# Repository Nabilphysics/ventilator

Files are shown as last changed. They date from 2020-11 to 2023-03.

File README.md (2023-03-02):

# Turbine Based Open-source Medical Ventilator [][License]

*A Turbine Based Medical Ventilator*

---
Publication 1: HardwareX :https://www.hardware-x.com/article/S2468-0672(22)00095-5/fulltext </br>
Publication: https://dl.acm.org/doi/abs/10.1145/3502871.3502893
</br> 
<div align = 'center'>

  **⸢ [Website] ⸥**
  **⸢ [Videos] ⸥**
  
</div>

---

<br>

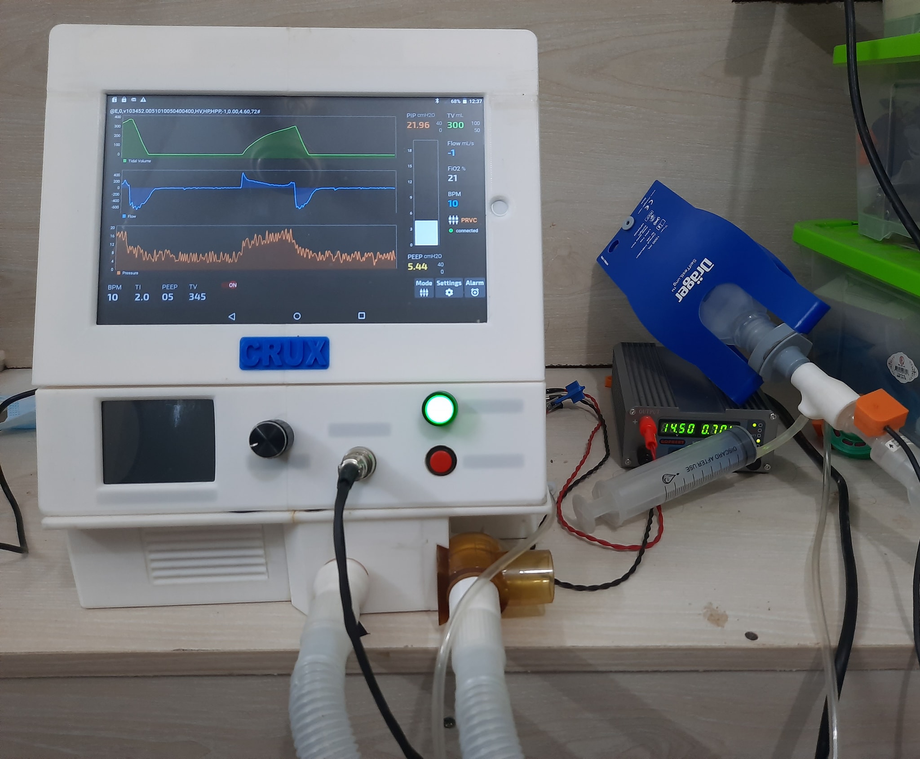
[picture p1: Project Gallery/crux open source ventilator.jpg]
Machine
 

<br>
<br>

## Concept

<br>

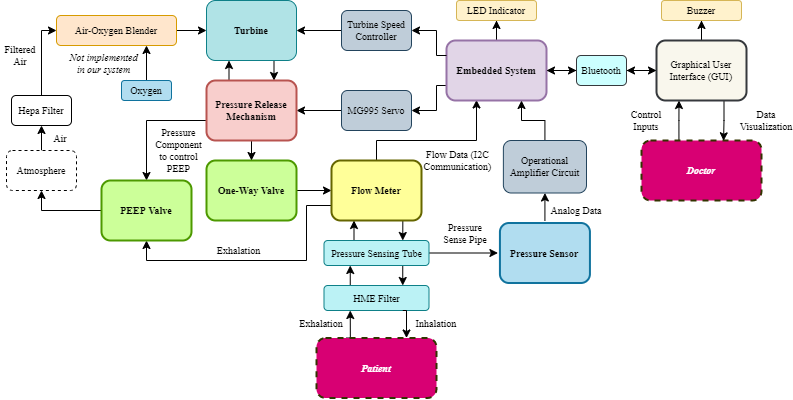
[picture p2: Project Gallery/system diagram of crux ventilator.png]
Concept


<br>
<br>

## Team

<br>

**Syed Razwanul Haque Nabil** 
[][Nabil LinkedIn]
[][Nabil Facebook]

- `Team Lead`
- `Algorithm`
- `Circuit`
- `Code`

<br>

**Maruf Hossain Rahat**

- `Mechanical Design Lead`
- `Research`

<br>

**Shovon S Saha**

- `Documentation`
- `Research`

<br>

**Fozlerabbi Shafi**

- `GUI App`

<br>

**Hasan Sohag**

- `Mechanical Design`
- `Assembling`

<br>

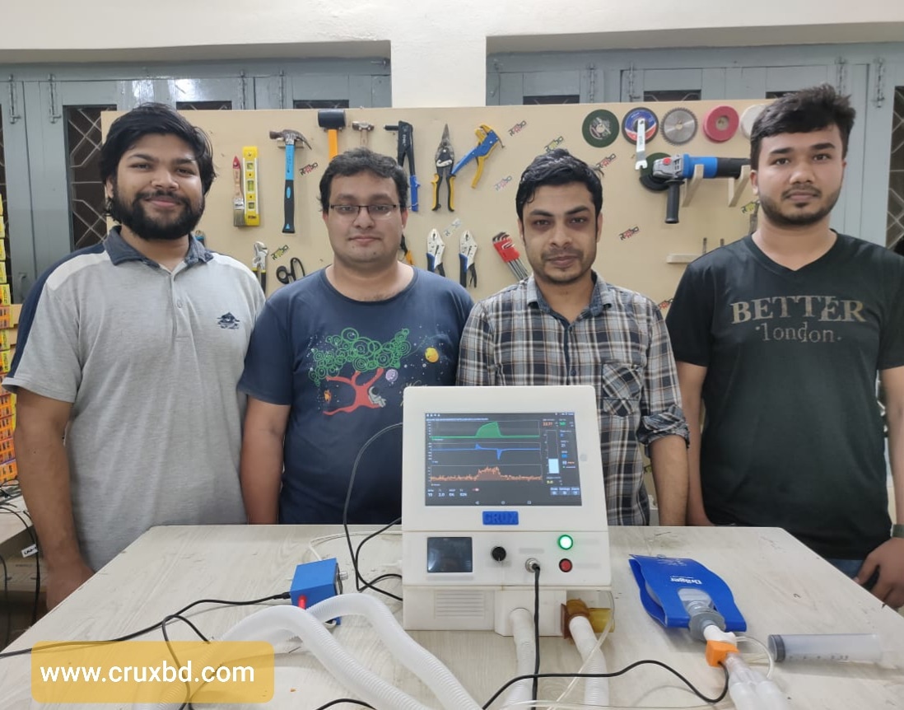
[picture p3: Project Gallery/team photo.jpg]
Team


<!----------------------------------------------------------------------------->

[Website]: https://www.nabilbd.com/ventilator
[Videos]: https://www.youtube.com/playlist?list=PLWOXOpFr-Z50Q3X0qPz6WNfCwyVcnYaeS 

[License]: LICENSE

<!----------------------------------{ Badges }--------------------------------->

[Badge Facebook]: https://img.shields.io/badge/Facebook-1877F2?style=for-the-badge&logo=facebook&logoColor=white
[Badge LinkedIn]: https://img.shields.io/badge/LinkedIn-0077B5?style=for-the-badge&logo=linkedin&logoColor=white
[Badge License]: https://licensebuttons.net/l/by-sa/4.0/80x15.png

<!-------------------------------{ Contributors }------------------------------>

[Nabil Facebook]: https://www.fb.com/Nabilphysics
[Nabil LinkedIn]: https://www.linkedin.com/in/nabilphysics/

<!----------------------------------{ Photos }--------------------------------->

[Concept]: Project%20Gallery/system%20diagram%20of%20crux%20ventilator.png
[Machine]: Project%20Gallery/crux%20open%20source%20ventilator.jpg
[Team]: Project%20Gallery/team%20photo.jpg

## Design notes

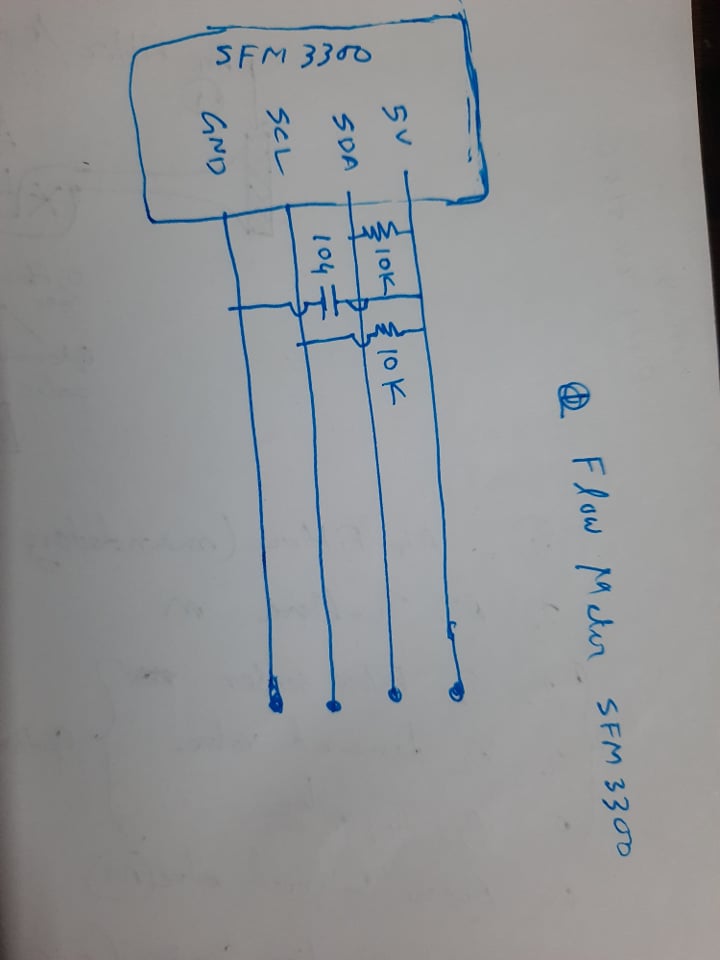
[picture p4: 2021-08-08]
Electronics/sfm3300 flow sensor connector circuit.jpg

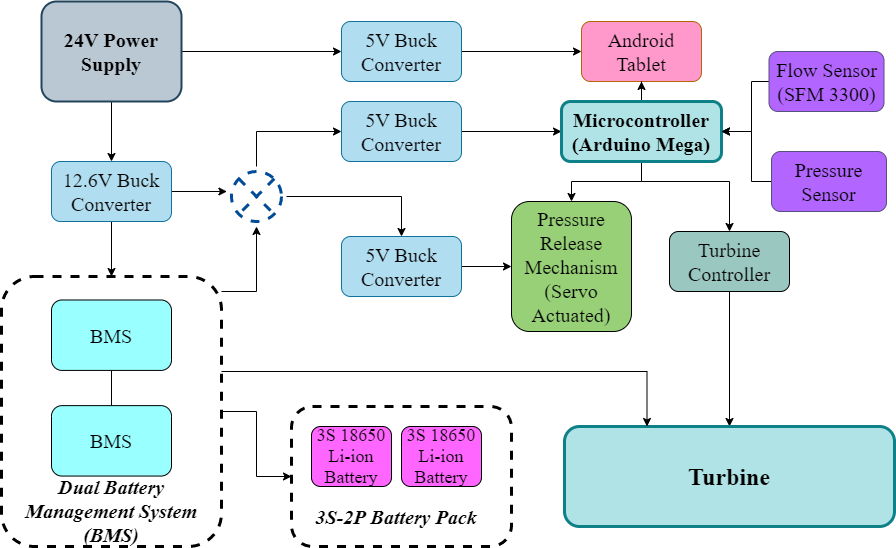
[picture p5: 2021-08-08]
Project Gallery/Electronics Modules' Integration.png

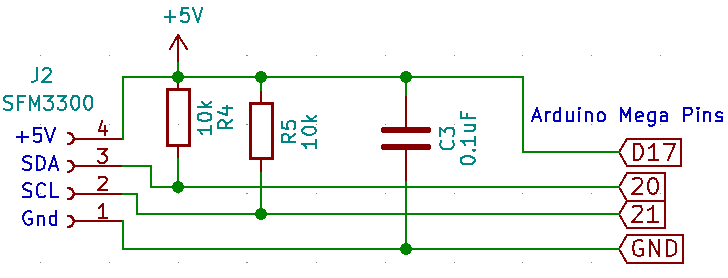
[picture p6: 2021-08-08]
Electronics/SFM3300 Circuit.png

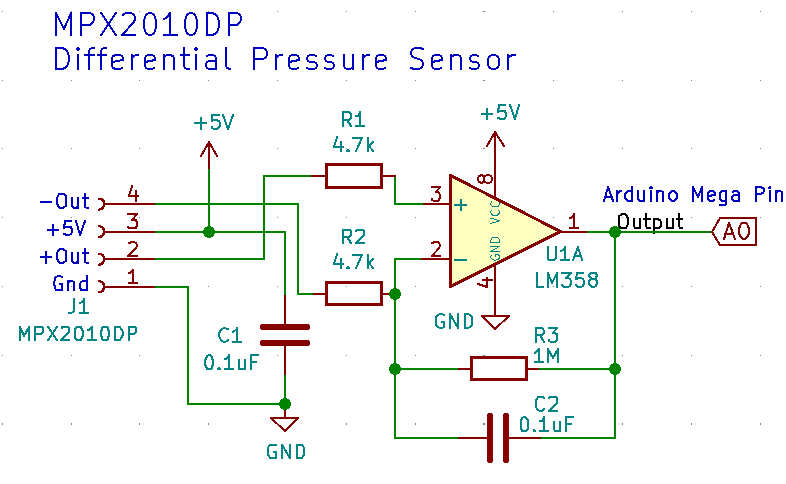
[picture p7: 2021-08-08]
Electronics/MAX2010DP Amplfier Circuit.png

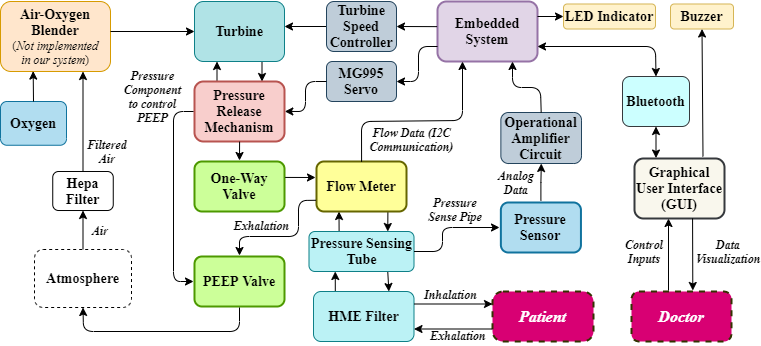
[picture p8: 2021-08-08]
Project Gallery/System Architecture.png

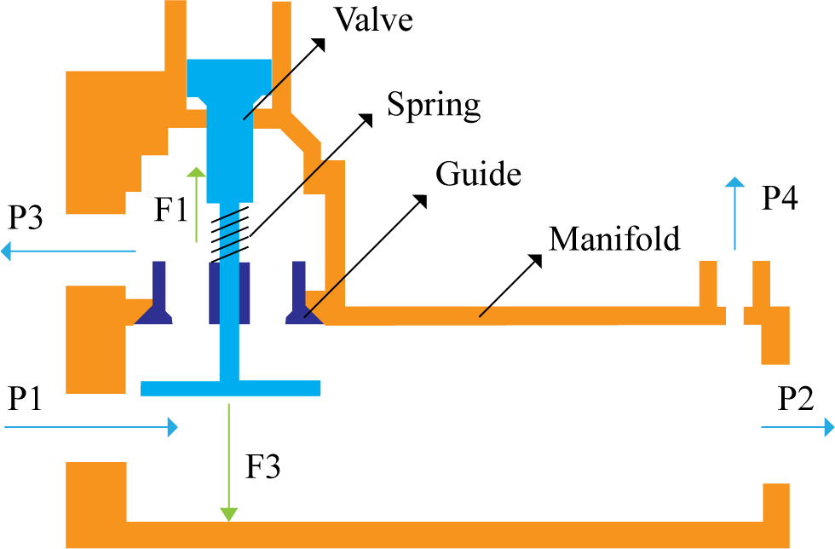
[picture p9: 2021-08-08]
Project Gallery/Free-body diagram of PRM during exhale.png

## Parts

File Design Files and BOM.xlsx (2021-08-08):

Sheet: Design Files
Design file name | File type | Open-source license
base 11 | CAD files (STEP) | CC BY-SA 4.0
base 12 | CAD files (STEP) | CC BY-SA 4.1
base 21 | CAD files (STEP) | CC BY-SA 4.2
base 22 | CAD files (STEP) | CC BY-SA 4.3
top 22 | CAD files (STEP) | CC BY-SA 4.4
top 21 | CAD files (STEP) | CC BY-SA 4.5
debug cover | CAD files (STEP) | CC BY-SA 4.6
charging port | CAD files (STEP) | CC BY-SA 4.7
top 11 | CAD files (STEP) | CC BY-SA 4.8
top 12 | CAD files (STEP) | CC BY-SA 4.9
front 11 | CAD files (STEP) | CC BY-SA 4.10
back 11 | CAD files (STEP) | CC BY-SA 4.11
back 12 | CAD files (STEP) | CC BY-SA 4.12
front 12 | CAD files (STEP) | CC BY-SA 4.13
Side Vent v1 | CAD files (STEP) | CC BY-SA 4.14
Tab Cover 1 | CAD files (STEP) | CC BY-SA 4.15
Tab Cover 2 | CAD files (STEP) | CC BY-SA 4.16
Button1 v1 | CAD files (STEP) | CC BY-SA 4.17
Button2 v1 | CAD files (STEP) | CC BY-SA 4.18
Air Filter Vent v1 | CAD files (STEP) | CC BY-SA 4.19
Front Extension 1 (Base) | CAD files (STEP) | CC BY-SA 4.20
Front Extension 1 (Attachment | CAD files (STEP) | CC BY-SA 4.21
Front Extension 2 v1 | CAD files (STEP) | CC BY-SA 4.22
Pressure Hose Attachment v1 | CAD files (STEP) | CC BY-SA 4.23
Indicator v1 | CAD files (STEP) | CC BY-SA 4.24
Push Button v1 | CAD files (STEP) | CC BY-SA 4.25
DMX 5pin v1 | CAD files (STEP) | CC BY-SA 4.26
Rotary Encoder Module v1 | CAD files (STEP) | CC BY-SA 4.27
Knob 20mm v1 | CAD files (STEP) | CC BY-SA 4.28
Power Socket v1 | CAD files (STEP) | CC BY-SA 4.29
Switch DPDT v1 | CAD files (STEP) | CC BY-SA 4.30
DC Power Socket v1 | CAD files (STEP) | CC BY-SA 4.31
LCD Holder 1 | CAD files (STEP) | CC BY-SA 4.32
LCD Holder 2 | CAD files (STEP) | CC BY-SA 4.33
LCD Holder 3 | CAD files (STEP) | CC BY-SA 4.34
2.8_TFT_LCD_Display v1 | CAD files (STEP) | CC BY-SA 4.35
3mm Pin | CAD files (STEP) | CC BY-SA 4.36
Tab v1 | CAD files (STEP) | CC BY-SA 4.37
Holder1 | CAD files (STEP) | CC BY-SA 4.38
Holder2 | CAD files (STEP) | CC BY-SA 4.39
Support | CAD files (STEP) | CC BY-SA 4.40
Holder3 | CAD files (STEP) | CC BY-SA 4.41
Outlet Body | CAD files (STEP) | CC BY-SA 4.42
Outlet Base | CAD files (STEP) | CC BY-SA 4.43
Exhaust Valve Gate v1 | CAD files (STEP) | CC BY-SA 4.44
Stopper Bolt | CAD files (STEP) | CC BY-SA 4.45
Stopper Gasket | CAD files (STEP) | CC BY-SA 4.46
EOM(Base) | CAD files (STEP) | CC BY-SA 4.47
EOM (Push Body) | CAD files (STEP) | CC BY-SA 4.48
EOM (Servo Bracket) | CAD files (STEP) | CC BY-SA 4.49
Silicon Seal | CAD files (STEP) | CC BY-SA 4.50
Screw | CAD files (STEP) | CC BY-SA 4.51
EGV Base | CAD files (STEP) | CC BY-SA 4.52
MG995 v1 | CAD files (STEP) | CC BY-SA 4.53
Servo Horn v1 | CAD files (STEP) | CC BY-SA 4.54
Exhaust Gate Valve Coil Spring v1 | CAD files (STEP) | CC BY-SA 4.55
One Way Valve Inlet | CAD files (STEP) | CC BY-SA 4.56
One Way Valve Outlet | CAD files (STEP) | CC BY-SA 4.57
Adapter_14mm (Long) v1 | CAD files (STEP) | CC BY-SA 4.58
Adapter14mm v1 | CAD files (STEP) | CC BY-SA 4.59
WM7040 Pump v1 | CAD files (STEP) | CC BY-SA 4.60
HME Body | CAD files (STEP) | CC BY-SA 4.61
HME Cover | CAD files (STEP) | CC BY-SA 4.62
HME Inlet Mesh | CAD files (STEP) | CC BY-SA 4.63
Inlet Body v1 | CAD files (STEP) | CC BY-SA 4.64
Proportional Valve Body | CAD files (STEP) | CC BY-SA 4.65
Proportional Valve Cover | CAD files (STEP) | CC BY-SA 4.66
Adapter_14mm (Short) v1 | CAD files (STEP) | CC BY-SA 4.67
Adapter_14mm (Pump Outlet) v1 | CAD files (STEP) | CC BY-SA 4.68
Micro Tower 9g v1 | CAD files (STEP) | CC BY-SA 4.69
peep inlet | CAD files (STEP) | CC BY-SA 4.70
peep outlet | CAD files (STEP) | CC BY-SA 4.71
Peep Extension | CAD files (STEP) | CC BY-SA 4.72
Peep Valve Attachment | CAD files (STEP) | CC BY-SA 4.73
Hose_OXY | CAD files (STEP) | CC BY-SA 4.74
Hose_Release | CAD files (STEP) | CC BY-SA 4.75
Peep Hose | CAD files (STEP) | CC BY-SA 4.76
OXY Nozzle Body | CAD files (STEP) | CC BY-SA 4.77
OXY Nozzle Holder | CAD files (STEP) | CC BY-SA 4.78
PSU mount v1 | CAD files (STEP) | CC BY-SA 4.79
SMPS v1 | CAD files (STEP) | CC BY-SA 4.80
3S Battery Holder v1 | CAD files (STEP) | CC BY-SA 4.81
PANASONIC_NCR-18650B v1 | CAD files (STEP) | CC BY-SA 4.82
Holder | CAD files (STEP) | CC BY-SA 4.83
PSU Holder Tab v1 | CAD files (STEP) | CC BY-SA 4.84

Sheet: BOM
Designator | Component | Number | Cost Per Unit (USD) | Total Cost (USD) | Source
WM7040 Pump v1 | Turbine | 1 | 53 | 53 | https://www.aliexpress.com/item/10000048326249.html?spm=a2g0s.8937460.0.0.438c2e0ePyDUwe
 | SFM3300-250-D Flow Sensor | 1 | 45 | 45 | https://www.digikey.com/en/products/detail/sensirion-ag/SFM3300-250-D/9857673
 | Pressure Sensor- MPX2010DP | 1 | 19 | 19 | https://www.digikey.com/en/products/detail/nxp-usa-inc/MPX2010DP/410890?s=N4IgTCBcDaILYAcAeYAMBGVATBIC6AvkA
 | Arduino Mega | 1 | 9.49 | 9.49 | https://cutt.ly/zmbwZLd
 | Buck Converter - XL4015 | 3 | 1.3 | 3.9 | https://cutt.ly/xl4015
 | Buck Converter - LM2596 | 1 | 1 | 1 | https://cutt.ly/lm2596
 | Digital Encoder | 1 | 1 | 1 | https://cutt.ly/1mv4wQJ
MG995 v1 | MG995 Servo | 1 |  | 2 | https://cutt.ly/Smv7uFC
Micro Tower 9g v1 | Sg90 Micro Servo | 1 | 1 | 1 | https://cutt.ly/bmv7vfv
 | Op Amp LM358 | 1 | 0.53 | 0.53 | https://www.digikey.com/en/products/detail/texas-instruments/LM358PE4/1510269
 | Diode MBR20100 | 1 | 1.07 | 1.07 | https://www.digikey.com/en/products/detail/smc-diode-solutions/MBR20100/6022125
 | 4.7K Ohms Resistor | 2 | 0.26 | 0.52 | https://www.digikey.com/en/products/detail/vishay-beyschlag-draloric-bc-components/MBB02070C4701FCT00/7351222
 | 10K Ohm Metal Film Resistor | 2 | 0.4 | 0.8 | https://www.digikey.com/en/products/detail/vishay-beyschlag-draloric-bc-components/PR02000201002JA100/7351718
 | 1M Ohm Resistor | 1 | 0.26 | 0.26 | https://www.digikey.com/en/products/detail/vishay-beyschlag-draloric-bc-components/MRS25000C1004FRP00/5063981
 | Capacitor 104/100nF | 2 | 0.45 | 0.9 | https://www.digikey.com/en/products/detail/vishay-beyschlag-draloric-bc-components/K104K15X7RF53H5G/13279844
Tab v1 | Android Tab 10.11” Touch Screen | 1 | 95 | 95 | https://www.bdstall.com/details/5-star-2gb-ram-tablet-pc-50422/
2.8_TFT_LCD_Display v1 | 3.2 TFT Display | 1 | 11.61 | 11.61 | https://cutt.ly/omv3c9n
PANASONIC_NCR-18650B v1 | 18650 Battery | 6 | 3.65 | 21.9 | https://cutt.ly/xmv9Gkt
 | BMS 3S1P | 2 | 1 | 2 | https://cutt.ly/Omv8Q3u
3S Battery Holder v1 | Battery Spacer | 4 | 0.24 | 0.96 | https://cutt.ly/dm6nxyz
 | USB Cable 1 meter | 1 | 3 | 3 | https://www.aliexpress.com/item/4001177937131.html
DMX 5pin v1 | GX12-5 Connector | 1 | 6 | 6 | https://www.banggood.com/Electronic-Soldering-Iron-GX12-5-Connector-T12-Aviation-Head-Mini-Aviation-Male-DIY-Soldering-Kits-p-1153612.html?cur_warehouse=CN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
 | Pogo Pins | 1 | 4.76 | 4.76 | https://www.digikey.com/en/products/detail/mill-max-manufacturing-corp/816-22-006-10-001101/6149708
 | Solderless docking type 4P, 5.08MM screw terminal | 3 | 0.5 | 1.5 | https://cutt.ly/4mx8ghB
DC Power Socket v1 | DC Jack Female | 1 | 0.2 | 0.2 | https://cutt.ly/rmv8rFg
 | USB Type A Standard Port Female | 1 | 0.1 | 0.1 | https://cutt.ly/Fmx8UJH
 | KF301-5.0-2P Green Connector | 1 | 0.1 | 0.1 | https://cutt.ly/Tmx4yFU
 | Straight Male Pin Header | 1 | 0.1 | 0.1 | https://cutt.ly/Kmx7BCz
 | Male Header L Shape | 1 | 0.8 | 0.8 | https://cutt.ly/rmv7ufC
 | L Connector
Power Socket v1 | Power Socket | 1 | 0.3 | 0.3 | https://cutt.ly/8mv8Ehn
 | TO220 Heat Sink | 1 | 0.5 | 0.5 | https://cutt.ly/qmx7H1O
 | Heat Shrink | 1 | 0.32 | 0.32 | https://cutt.ly/Cmv4PAG
 | Ventilator Patient Circuit | 1 | 6 | 6 | https://bmabazar.com/shop/ventilator-patient-circuit/
 | Viral Filter | 1 | 5 | 5 | https://bmabazar.com/shop/viral-filter/
 | PLA Filament for 3D Printing | 3 | 23 | 69 | https://www.sunlu.com/products/new-pla-plus-pla-1-75-filament-1kg-2-2lbs?variant=31987368788054
Screw | Screw Assortment Kit | 1 | 20 | 20 | https://www.aliexpress.com/item/33033655207.html
 | Epoxy Glue | 5 | 0.91 | 4.55 | https://www.aliexpress.com/item/1005002511958246.html
Exhaust Gate Valve Coil Spring v1 | Coil Spring: | 1 | 2.29 | 2.29 | https://www.aliexpress.com/item/4000411749473.html
 | (Length 25mm, Outer diameter 5mm, Wire thickness 0.3mm)
 | 10 pcs Pack
Stopper Gasket | Rubber O-ring kit | 1 | 4.35 | 4.35 | https://cutt.ly/nmWW9V6
 | 3mm Linear Rod (2 Pcs kit, 3mm*100mm) | 1 | 1.2 | 1.2 | https://cutt.ly/amSgoMs
Hose_OXY, Hose_Release | Silicon Tube 1 foot | 2 | 1.2 | 2.4 | https://cutt.ly/dm6mwlX
Silicon Seal | Silicone Sheet | 1 | 8.95 | 8.95 | https://cutt.ly/0mbtd5E
Peep Hose | 4mm Medical grade pipe | 1 | 4.99 | 4.99 | https://www.aliexpress.com/item/4000415201699.html
 | Heat Shrink Tube | 1 | 2.2 | 2.2 | https://cutt.ly/7mv5G4w
Peep Valve Attachment, Front Extension 1 (Attachment) | Extension Tube (4mm) | 1 | 8.86 | 8.86 | https://cutt.ly/emSfAHN

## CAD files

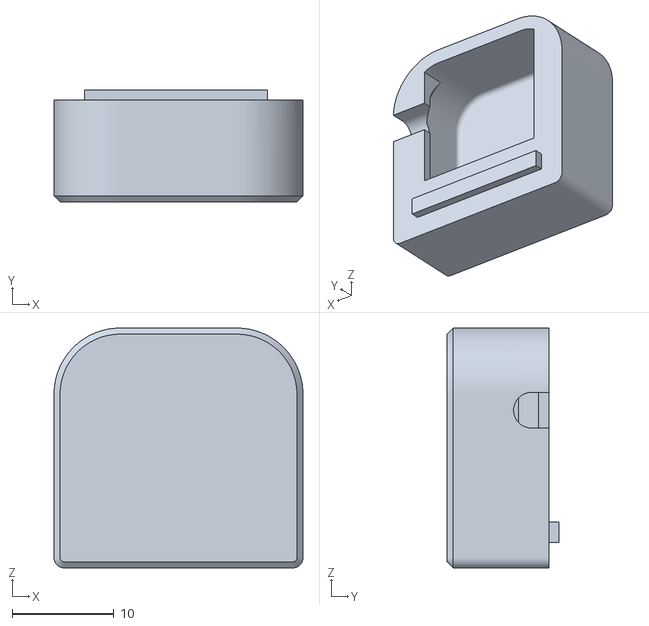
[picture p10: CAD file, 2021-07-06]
Assembly 3D Model Files/Flow Sensor Enclosure/sensor cover.stl
24.5 x 11.0 x 23.6

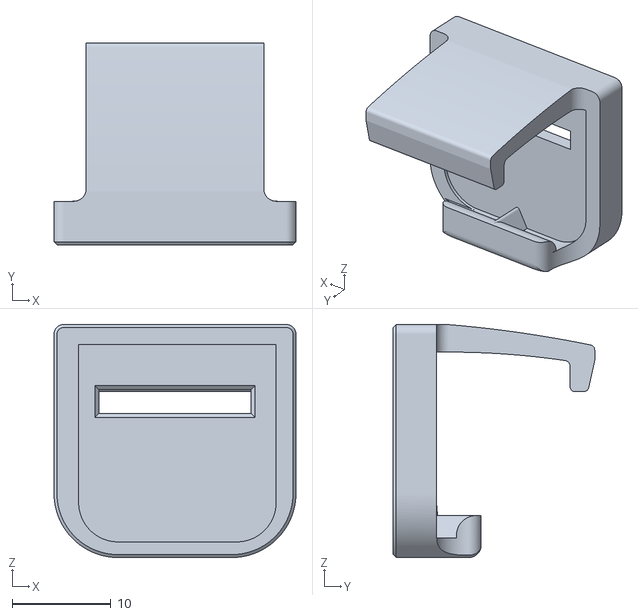
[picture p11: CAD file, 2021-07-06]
Assembly 3D Model Files/Flow Sensor Enclosure/sensor clip.stl
24.5 x 20.4 x 23.6

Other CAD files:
Assembly 3D Model Files/Flow Sensor Enclosure/Flow Sensor_Connector .f3d

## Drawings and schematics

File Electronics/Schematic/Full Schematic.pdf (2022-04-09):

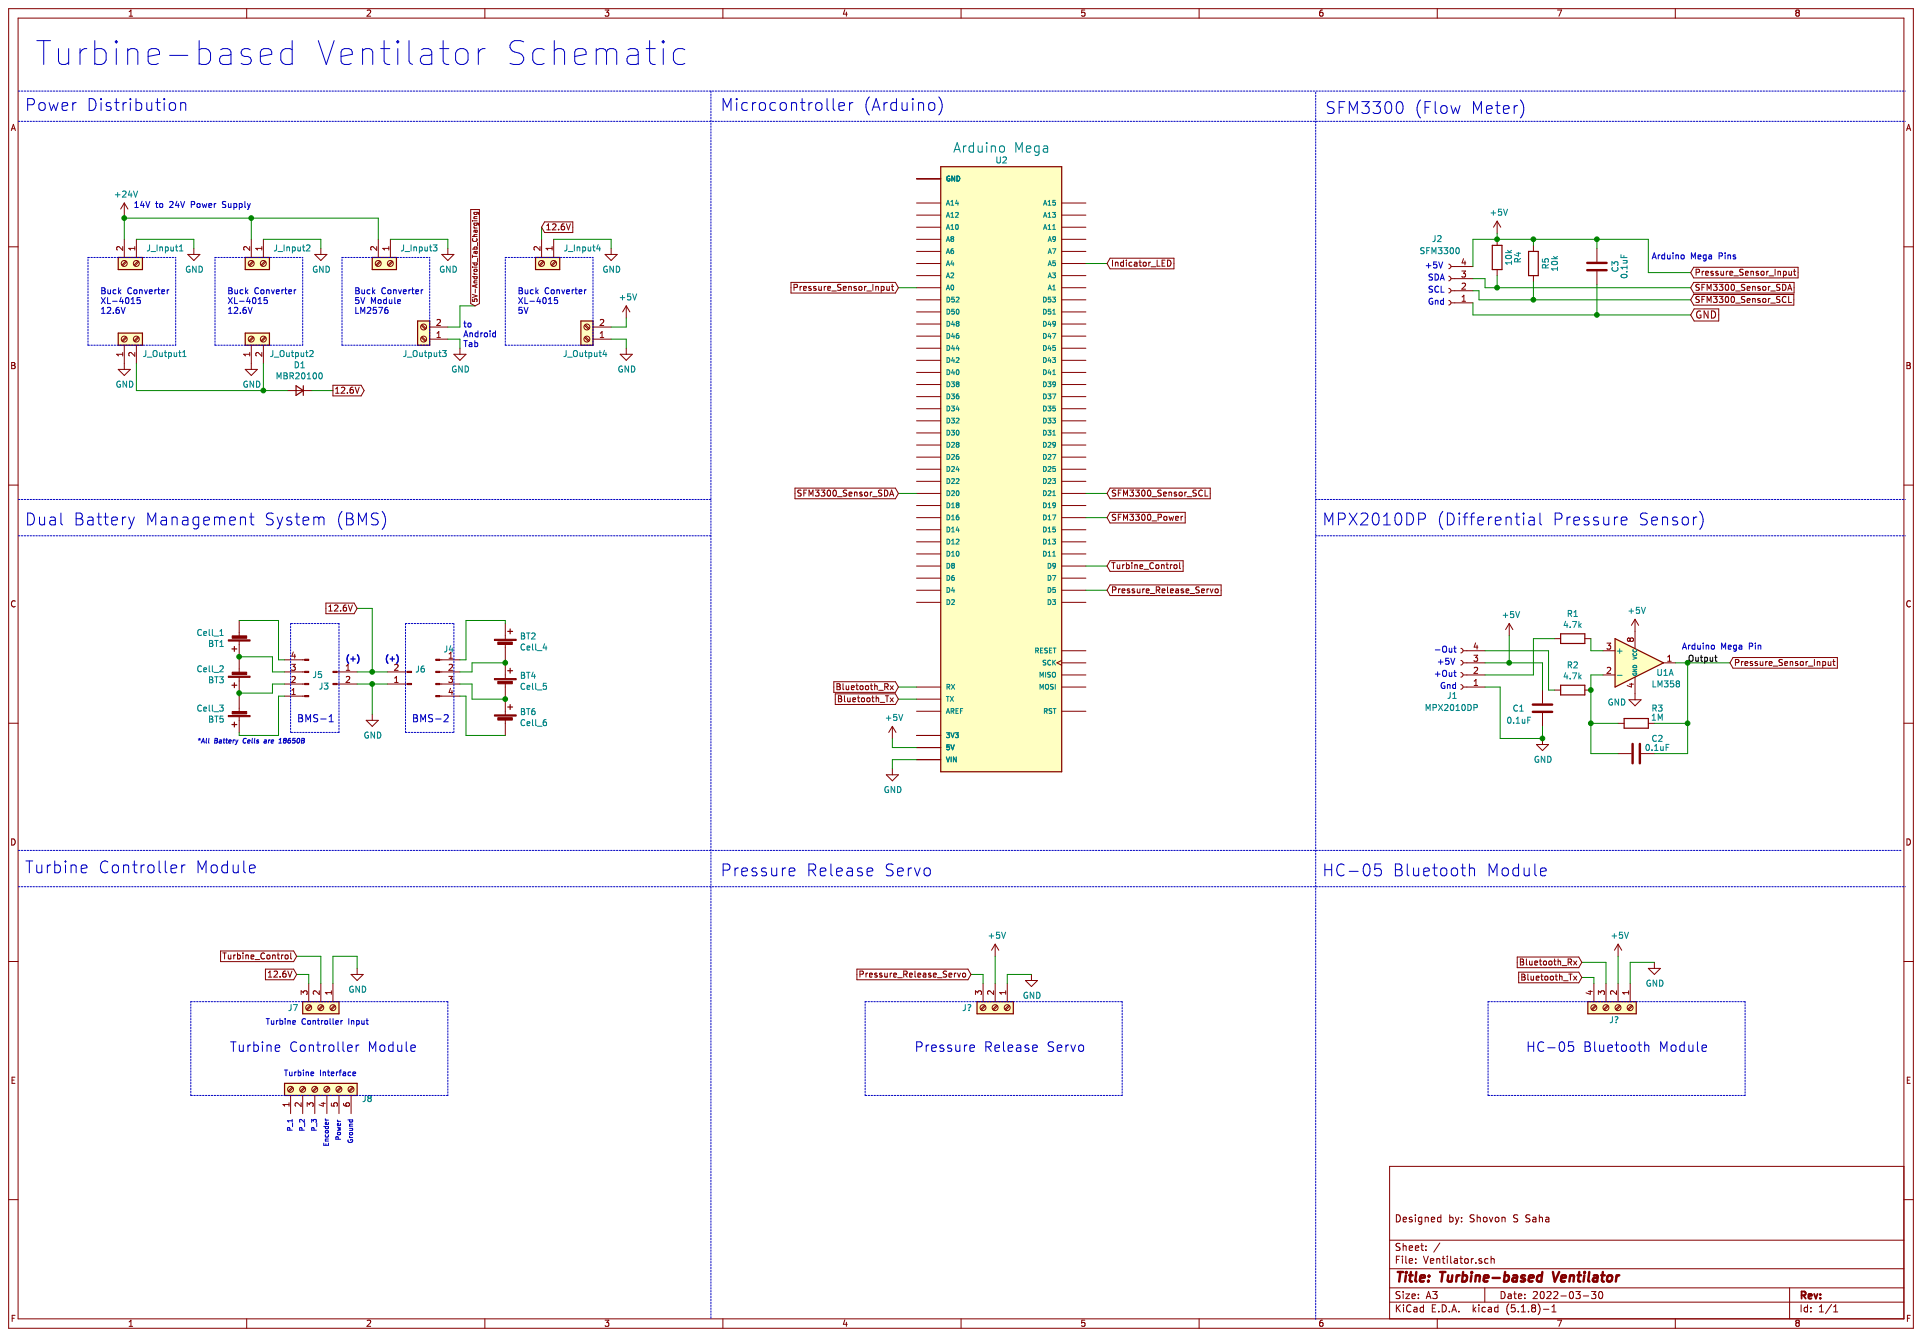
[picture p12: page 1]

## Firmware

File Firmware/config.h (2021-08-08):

#ifndef CONFIG_H
#define CONFIG_H

//////////Ventilator Hardware Pin//////////////
//Hardware Connection: 

//Servo 1 > Servo One(Pressure Release Servo) > Pin 5
//pin:9 > turbine motor(bldc or dc: currently being used for turbine control) 
//A0: > Pressure Sensor, 
//D17: > FlowSensorPower(5V)
// Indicator LED > A5
//Left to Right- VDD,SCL(21),GND,SDA(20) - Arduino Mega
//Sensirion Flow Sensor: Left to Right- VDD,SCL(Arduino - 21),GND,SDA(Arduino - 20) - Arduino Mega
//Unused in this version
//Pin:11 > servo or relay (for BLDC Version)
//Servo 2 > ArduinoMega Pin 52

//////// Select Motor Type /////////////
//#define bldcMotor
#define dcMotor
//////////// I/O Pin Defination ////////////////////
const byte flowSensorOnOff = 17;
const byte turbineMotorPin = 9;
const byte flowSenseMpx7002Pin = 14;//A14
const byte pressureSenseMpx2010Pin = 0; //A0
const byte indicatorLed = A5;

//////// Universal Variable  ////////
boolean disconnectFlagAllModes;
float flowSensorError = 0;//in ml
int flowRateAllModes;
float continuousVolumeChangeAllModes;
uint8_t motorSpeedAllModes;
float pressureAllModes;
uint8_t timeAfterDataShow = 40; //ms , it determines data sending interval to Android Application
uint8_t stabilizingCounter = 0;

float timex;
float timey;
float timeDifference;






#ifdef dcMotor
//////////// Servo Pin ///////////////
Servo servoOne;
Servo servoTwo;
Servo oxygenServo;
Servo airServo;
Servo peepServo;
const byte servoOnePin = 5; // pressure release servo
const byte servoTwoPin = 52;
const byte oxygenServoPin = 46;
const byte airServoPin = 48;

uint8_t servoCloseValue = 56; //High Pressure
uint8_t servoOpenValue = 90; // Low Pressure
uint8_t oxygenServoFullOpenValue = 170;
//uint8_t oxygenServo;

uint8_t motorSpeed = 30; //initial inspiratory motor speed as Feed Forward
uint8_t motorSpeedMin = 20; //Feed Forward
uint8_t motorSpeedMax = 140; // To impose Hard Prassure Limit as security
float motorPEEPSpeed = 30; //Feed Forward
float motorPEEPSpeedMax = 150;
float motorPEEPSpeedMin = 20;
#endif

//////////Start CPAP Mode Settings //////////////
#ifdef dcMotor
int motorBaseSpeedCpap = 10;
int motorSpeedMaxCpap = 150;
int motorSpeedMinCpap = 0;
float cpapPressureMax = 20.0;
float cpapRampTime;
float cpapPidProportionalConstant;

#endif




//////////End CPAP Mode Settings//////////////

#endif

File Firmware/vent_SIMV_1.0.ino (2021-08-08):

/*
 * CRUX Open Source Ventilator
  https://www.cruxbd.com 
  Version: Demo 4.0
  Team Member:
  1) Syed Razwanul Haque(Nabil)
     https://www.nabilbd.com/ventilator
   Team Lead, Research, Coding
  2) Maruf Hossain
   Research, Mechanical & 3D Design
  Licensing Under Processing
  3) Shafi
     UI Software
  4) Hasan
     3D Design, Assembling
  5) Shovon S Saha, shovonsaha3401@gmail.com
     General Research, Documentation, Scientific Paper
 */  
 /*
  * SIMV Mode works with PRVC mode (ToDo: SIMV with Pressure Control Mode)
  * SIMV with Support mode not incorporated
  * 
  */
#include <Arduino.h>
#include <Servo.h>
#include <Wire.h>
#include "config.h"
#include "gasblending.h"
#include "callibration.h"
#include "volume.h"
#include "pressure.h"
#include "datafilter.h"
#include "sensor.h"
#include "showdata.h"
#include "alarm.h"
#include "SFM3000CORE.h"

SFM3000CORE sensirionFlow(64); //Sensirion Flow Sensor Object
//Left to Right- VDD,SCL(A5),GND,SDA(A4)
// To Do: Replace minimum variable size needed. e.g. uint8_t insteed of int where applicable
// To Do: Make the code object orienteed. Create Separate Method to Write Motor Speed
//////////Data Frame Variable//////////
String getVentFrame; // Data String Received from Android Tab as a Frame. e.g.  getVentFrame = "v061502.0042090050025150702";
String mode;
uint8_t bpm;
int Tv;
int Ti;
int Te;
float nonSyncTime;  // for SIMV
float syncTime;
float peep;
int pip;
int breathCycleTime;
float targetFlowRate;
/// Variables for Alarm
int TvAlarmHigh;
int TvAlarmLow;
int peepAlarmHigh;
int peepAlarmLow;
int pipAlarmHigh;
int pipAlarmLow;
int simvTriggerFlow;
int simvOnOff;

//----------------------------------------------------------
void setup() {
  Serial.begin(115200);
  Serial.println("Started");
  Wire.begin(); // For Flow Sensor
  delay(1000); // Just for Stability
  pinMode(flowSensorOnOff, OUTPUT); // 5V Supply for Sensirion SFM3300 Flow Sensor. Since it require maximum 10ma so we are providing power from mcu pin 
  digitalWrite(flowSensorOnOff, HIGH); // SFM3300 Power Supply Started
  delay(100);
  sensirionFlow.init(); // Software Initialization of the SFM3300 Flow Sensor
  delay(1000);
 
#ifdef dcMotor //Actually Current Turbine from Aliexpress Although its a BLDC motor technically. Previously we used this pin to control a DC motor to provide PWM and write now providing PWM to BLDC Turbine
  pinMode(turbineMotorPin, OUTPUT);
  #endif
////////////////// Indicator LED //////////////////////////////
  pinMode(indicatorLed, OUTPUT);  //Green Big LED
////////////////// Servo Motor Initialization //////////////////
  servoOne.attach(servoOnePin); // Pressure Release Servo at Pin 5
  servoTwo.attach(servoTwoPin); // Not implemented
  oxygenServo.attach(oxygenServoPin);//In this version it has no real effects
  airServo.attach(airServoPin);//In this version it has no real effects
  peepServo.attach(40); // In this version it has no real effects
///////////////////////////////////////////////////////////////  
  oxygenServo.write(30);//In this version it has no real effects
  airServo.write(95);//In this version it has no real effects
  sensorCallibration(); // Pressure Senosr will be callibrated
  getVentFrame = "v061502.0042090050025150702"; //for testing purpose. In actual use please comment it out
 // getVentFrame = "p105001.5041090050025150702";
 // getVentFrame = "s";
    mode = getVentFrame.substring(0, 1); //e.g. v or p . v=PRVC mode p=PCV mode 
    bpm = getVentFrame.substring(1, 3).toInt(); //BPM=breath per minute . Two digit. e.g 06
    Tv = getVentFrame.substring(3, 6).toInt(); //Tidal Volume in ml , 3 digit. highest 999
    Ti = getVentFrame.substring(6, 9).toFloat() * 1000; //in millisecond
    peep = getVentFrame.substring(9, 11).toInt();
    pip = getVentFrame.substring(11, 13).toInt();
    TvAlarmHigh = getVentFrame.substring(13, 16).toInt(); // 3 digit, since highest 999
    TvAlarmLow = getVentFrame.substring(16,19).toInt();// 3 digit
    pipAlarmHigh = getVentFrame.substring(19,21).toInt(); //2 digit
    pipAlarmLow = getVentFrame.substring(21,23).toInt(); //2 digit
    peepAlarmHigh = getVentFrame.substring(23,25).toInt(); // 2 digit
    peepAlarmLow = getVentFrame.substring(25,27).toInt(); // 2 digit
  
//  mode = getVentFrame.substring(0, 1);
//  bpm = getVentFrame.substring(1, 3).toInt(); //BPM=breath per minute
//  Tv = getVentFrame.substring(3, 6).toInt(); //Tidal Volume in ml
//  Ti = getVentFrame.substring(6, 9).toFloat() * 1000; //in millisecond
//  peep = getVentFrame.substring(9, 11).toFloat();
//  pip = getVentFrame.substring(11, 13).toInt();
//  motorSpeed = getVentFrame.substring(13, 16).toInt();
  breathCycleTime = int((60 / float(bpm)) * 1000); //in millisecond. e.g. if BPM=10 , breath Cycle Time = 6000ms (Inpiration Time + Expiration Time)
  nonSyncTime = breathCycleTime * 0.9; //for SIMV Mode. to detect Sync Time. e.g. if breath cycle =10 then 9 is non sync period 
  Te = (breathCycleTime - Ti); //in millisecond, Te means Expiration Time during Exhale
  syncTime = nonSyncTime - Ti; //(in millisecond)in SIMV if trigger happens after this time period of Expiration then SIMV will give breath early
  
  targetFlowRate = Tv / ((float(Ti) / float(1000))); // in ml , not needed right now
 
  Serial.println("End of Setup");
}

void loop() {
  digitalWrite(indicatorLed, HIGH); // Green LED ON to indicate that device is operational
  if (Serial.available() > 0) {

    getVentFrame = Serial.readString(); 
    mode = getVentFrame.substring(0, 1);
    bpm = getVentFrame.substring(1, 3).toInt(); //BPM=breath per minute
    Tv = getVentFrame.substring(3, 6).toInt(); //Tidal Volume in ml
    Ti = getVentFrame.substring(6, 9).toFloat() * 1000; //in millisecond
    peep = getVentFrame.substring(9, 11).toInt();
    pip = getVentFrame.substring(11, 13).toInt();
    TvAlarmHigh = getVentFrame.substring(13, 16).toInt(); // 3 digits, since highest 999
    TvAlarmLow = getVentFrame.substring(16,19).toInt();// 3 digits
    pipAlarmHigh = getVentFrame.substring(19,21).toInt(); //2 digits
    pipAlarmLow = getVentFrame.substring(21,23).toInt(); //2 digits
    peepAlarmHigh = getVentFrame.substring(23,25).toInt(); // 2 digits
    peepAlarmLow = getVentFrame.substring(25,27).toInt(); // 2 digits
    simvTriggerFlow = getVentFrame.substring(27,29).toInt();//2 digits ,flow triggers ranging from 0.7 to 2.0 L/min - 11 ml/second to 50 ml/second
    simvOnOff = getVentFrame.substring(29,30).toInt();//1 digit, 1= SIMV ON , 0= SIMV OFF 

    breathCycleTime = int((60 / float(bpm)) * 1000); //in millisecond
    Te = (breathCycleTime - Ti); //in millisecond
    targetFlowRate = Tv / ((float(Ti) / float(1000))); // in ml
    nonSyncTime = breathCycleTime * 0.9; //for SIMV Mode. to detect Sync Time. e.g. if breath cycle =10 then 9 is non sync period 
    Te = (breathCycleTime - Ti); //in millisecond
    syncTime = nonSyncTime - Ti; //(in millisecond)in SIMV if trigger happens in this time period SIMV will give breath early
    //breathCycleTime = 20; Ti = 1000; Te = 2000;
  }
  //vent input=M,BPM,Tv(3 digit only),Ti,PEEP,PIP,TvAlarmHigh,TvAlarmLow,pipAlarmHigh,pipAlarmLow,peepAlarmHigh,peepAlarmLow
  //           V,20,999,1.5,05,20,900,500,25,15,07,02      //p155001.5052090050025150702

/// Restart Mechanism if Sensor Error Occured 
flowRate = sensirionFlow.getvalue();
   if((flowRate < -4500.0)||(flowRate > 4500.00)){ // if this condition satisfy that means error.
      Serial.println(flowRate);
      digitalWrite(flowSensorOnOff, LOW); // Sensor 5V Power OFF
      delay(1000);
      digitalWrite(flowSensorOnOff, HIGH); // Sensor 5V Power ON, for Hard Reset 
      delay(500);
      sensirionFlow.init();
      delay(50);
      sensirionFlow.softReset(); //Software Reset
      sensirionFlow.init();
      delay(1000);
      motorSpeed = 30; //Just to Run Slowly
     //To Do = Create Flow Sensor Error Alarm
    }

  ///Volume Control Mode//////
  if (mode == "v") {
   
    volumeControl(); //PRVC
    //inspiratoryLoop();
  }
  
  if (mode == "p") { //PCV = Pressure Control Ventilation
    //stabilizingCounter = 0;
    pressureControl();
  }
  
  if (mode == "s"){ //Debugging Mode. Its not actually a mode. Its for Testing. It will just execute below procedure. 
    analogWrite(turbineMotorPin,0);
    
    //servoControl("close");
    float flowResult = sensirionFlow.getvalue();
    Serial.print(" Pressure=");
    Serial.print(pressureSenseMpx2010(pressureSenseMpx2010Pin));
    Serial.print(" SensirionML/S=");
    Serial.print(flowResult);
    Serial.print(" SensirionSLM=");
    Serial.println((flowResult*60)/1000);
    delay(100);
    servoControl("open");
    flowResult = sensirionFlow.getvalue();
    Serial.print(" Pressure=");
    Serial.print(pressureSenseMpx2010(pressureSenseMpx2010Pin));
    Serial.print(" SensirionML/S=");
    Serial.print(flowResult);
    Serial.print(" SensirionSLM=");
    Serial.println((flowResult*60)/1000);
    
    delay(100);

    //peepServo.write(1);
  
    
    
    //servoControl("open");
    //analogWrite(turbineMotorPin,0);
    //Serial.print(" Pressure=");
    //Serial.print(pressureSenseMpx2010(pressureSenseMpx2010Pin));
   
    //delay(3000);
    //delay(40);

    //     bldc.write(15);
//    servoControl("open");
//    delay(5000);
//    servoControl("close");
//    delay(5000);
    
//    float arrayData[] = {4.81,4.81,5.02,5.02,5.02,5.02,5.02,5.23,5.02,5.23,5.44,5.23,5.44,5.02,5.44,5.44,5.44};
//    Serial.println(dataFilter(arrayData,sizeof(arrayData)/sizeof(float)));
//    servoControl("open");
//    delay(1000);
//    bldc.write(15);
//    serialDataOutVolumeControl("Stop");
//float testData[] = {10.1,2.0 , 6.0, 2.0 , 1.0, 7.0, 7.6,8.9,7.6};
//Serial.println(highestPressureCalculator(testData, sizeof(testData)/sizeof(float)));
  }
 
  
  

}

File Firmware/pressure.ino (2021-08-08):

void pressureControl() {

  /////////////////////inspiratory Phase///////////////
  volume = 0;
  //pressureTi = Ti;
  //pressureTe = Te;
  targetPressure = pip;
  targetPEEPPressure = peep;
  for (timeSumming = 0; timeSumming < Ti ; timeSumming = timeSumming + timeDiff) {
    int time1 = millis();
    servoControl("close");
    if (disconnectFlagPressureMode == true) {
#ifdef bldcMotor
      bldc.write(initialPressureMotorSpeed);
#endif
#ifdef dcMotor
      analogWrite(turbineMotorPin, initialPressureMotorSpeed);
#endif

    }
    else {
#ifdef bldcMotor
      bldc.write(pressureMotorSpeed);
#endif
#ifdef dcMotor
      analogWrite(turbineMotorPin, pressureMotorSpeed);
#endif
    }
    //pressureControlModeflowRate = flowRateMpx7002Sensor(flowSenseMpx7002Pin);
    pressureControlModeflowRate = sensirionFlow.getvalue();
    delay(3);
    volume = pressureControlModeflowRate * (timeDiff / 1000) + volume;     // Tidal Volume in ml
    timeTrack = timeTrack + timeDiff;

    flowRateAllModes = pressureControlModeflowRate;
    //continuousVolumeChangeAllModes = volumePressureMode;
    motorSpeedAllModes = pressureMotorSpeed;

    int time2 = millis();
    timeDiff = time2 - time1;

    if (timeTrack > timeAfterDataShow) {
      disconnectFlagAllModes = disconnectFlagPressureMode;
      realPressure = pressureSenseMpx2010(pressureSenseMpx2010Pin);
      pressureAllModes = realPressure;
      pError = targetPressure - realPressure;

      pressureMotorSpeed = initialPressureMotorSpeed + pError * 3; //3= Kp, Proportional Constant 
      if (disconnectFlagPressureMode == true) {
        pressureMotorSpeed = initialPressureMotorSpeed;
      }
      if (pressureMotorSpeed < (initialPressureMotorSpeed - 20)) { //Lets say init speed = 50, so High=70, LOW=35
        pressureMotorSpeed = (initialPressureMotorSpeed - 20);
      }
      if (pressureMotorSpeed > (initialPressureMotorSpeed + 30)) {
        pressureMotorSpeed = (initialPressureMotorSpeed + 30);
      }



      ema = EMA_fun(0.15, realPressure, ema);
      ema_ema = EMA_fun(0.15, ema, ema_ema);

      float DEMA = 2 * ema - ema_ema;
      //Serial.print(disconnectFlagPressureMode);
      //Serial.print("inExpPressure= ");
      //Serial.print(realPressure);
      //Serial.print( "flow= ");
      //Serial.print(pressureControlModeflowRate);
      // Serial.print( "volume= ");
      // Serial.print(volumePressureMode);
      //      Serial.print(" DEMA= ");
      //      Serial.println(DEMA);
      //Serial.print(" Insp MotorSpeed=");
      //Serial.print(pressureMotorSpeed);
      //Serial.print(" Base Motor MotorSpeed=");
      //Serial.println(initialPressureMotorSpeed);
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

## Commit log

2020-11-06 circuit diagram high level
2020-12-18 41 files uploaded 3D printed mechanical parts
    41 files uploaded 3D printed mechanical parts
    [HME Cover.step, HME Inlet mesh.step, HME case.step, Inlet .step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]
2021-07-06 Flow Sensor Connector 3D files added
    [Flow Sensor_Connector .f3d, sensor clip.stl, sensor cover.stl]
2021-07-06 sfm3300 connector circuit
2021-08-08 Major reconstruction of files
    [Design Files and BOM.xlsx, Flow Sensor_Connector .f3d, HME Cover.step, HME Inlet mesh.step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]
2022-04-09 schematic & KiCad Files Added
    [Ventilator.kicad_pcb, Ventilator.sch]
